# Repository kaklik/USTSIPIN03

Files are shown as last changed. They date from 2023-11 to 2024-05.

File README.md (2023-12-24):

## USTSIPIN03 - Semiconductor based ionizing radiation dosimeter and spectrometer analog front-end

The USTSIPIN03 is developed as single board improved variant of the [PIND02](https://github.com/mlab-modules/PIND02) and [PCRD07](https://github.com/mlab-modules/PCRD07) modules from [MLAB.cz development system](https://www.mlab.cz/).  The analog front end is core part of the [AIRDOS04 cosmic radiation detector and dosimeter](https://github.com/UniversalScientificTechnologies/AIRDOS04). 

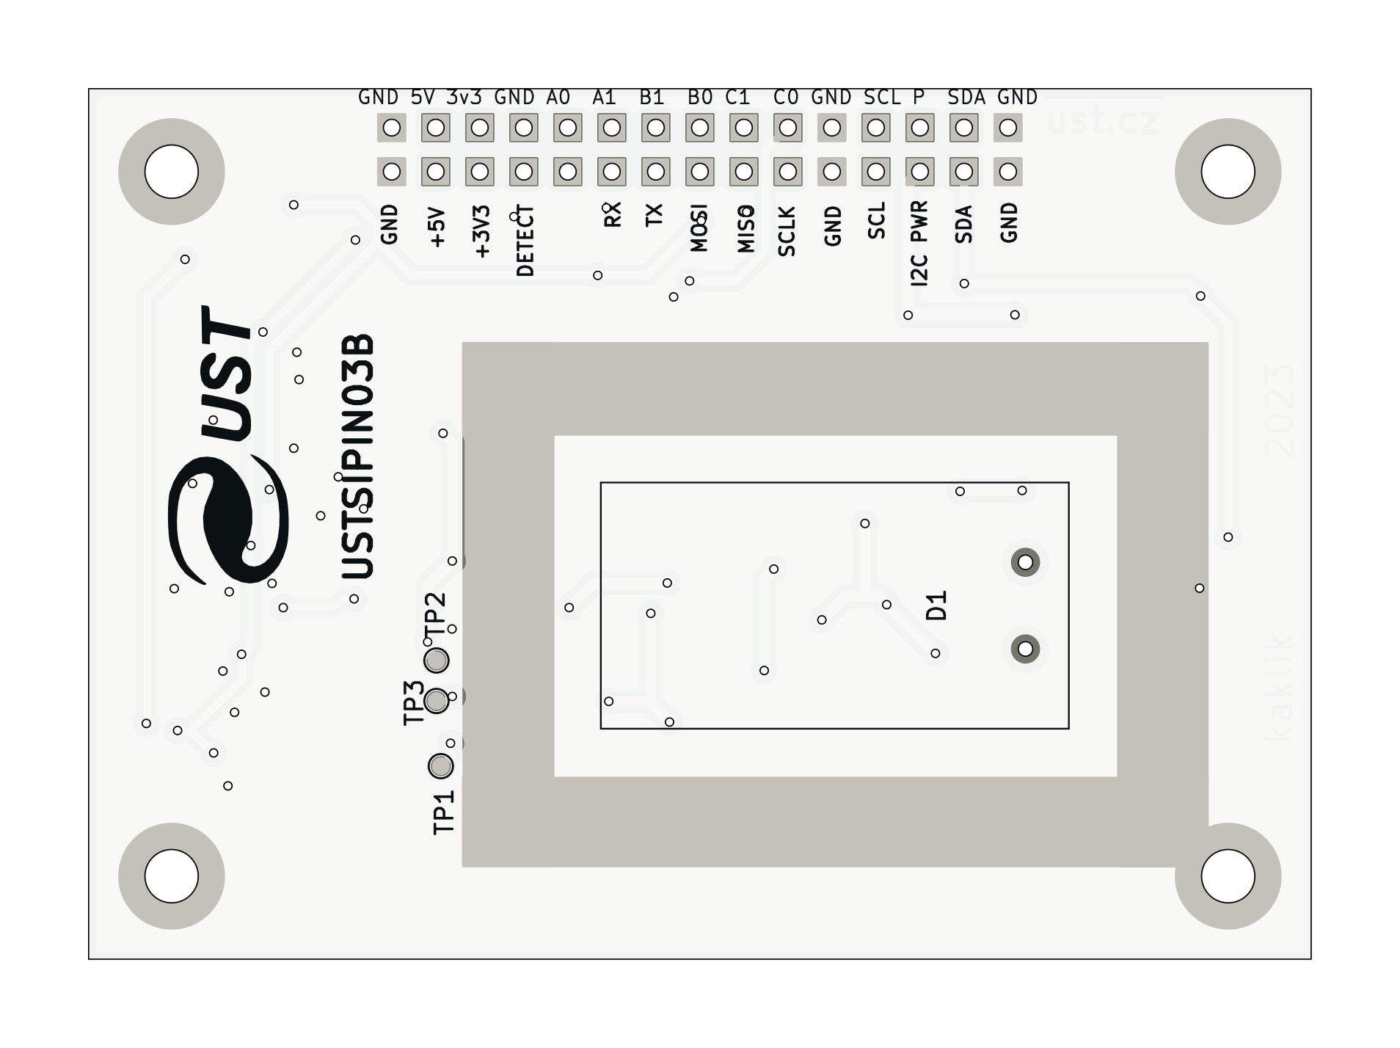
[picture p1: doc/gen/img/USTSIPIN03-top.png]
USTSIPIN03 Top view


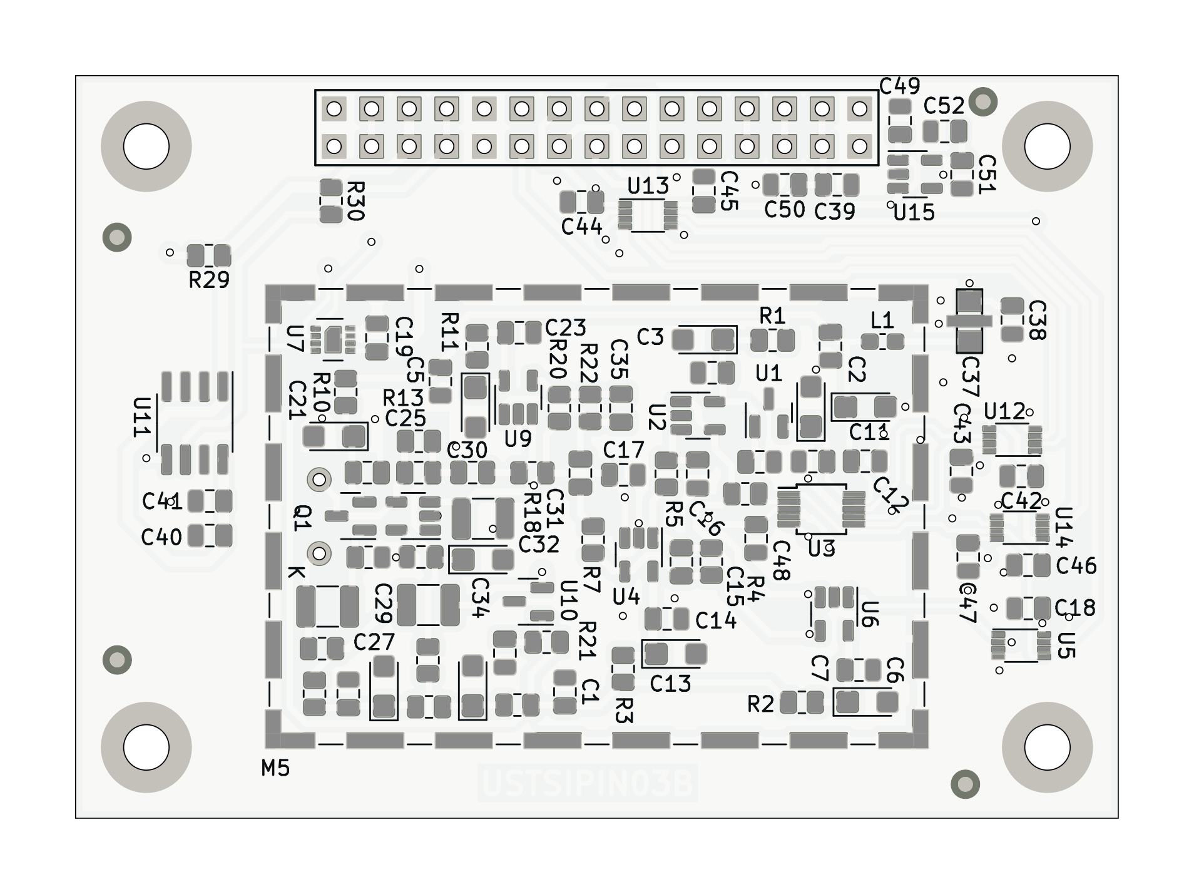
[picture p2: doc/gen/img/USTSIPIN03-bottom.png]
USTSIPIN03 Bottom view


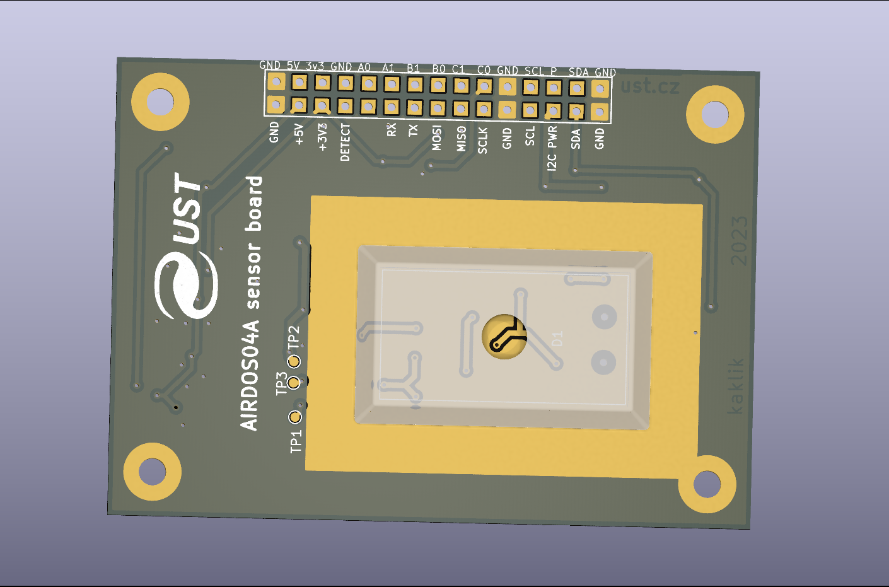
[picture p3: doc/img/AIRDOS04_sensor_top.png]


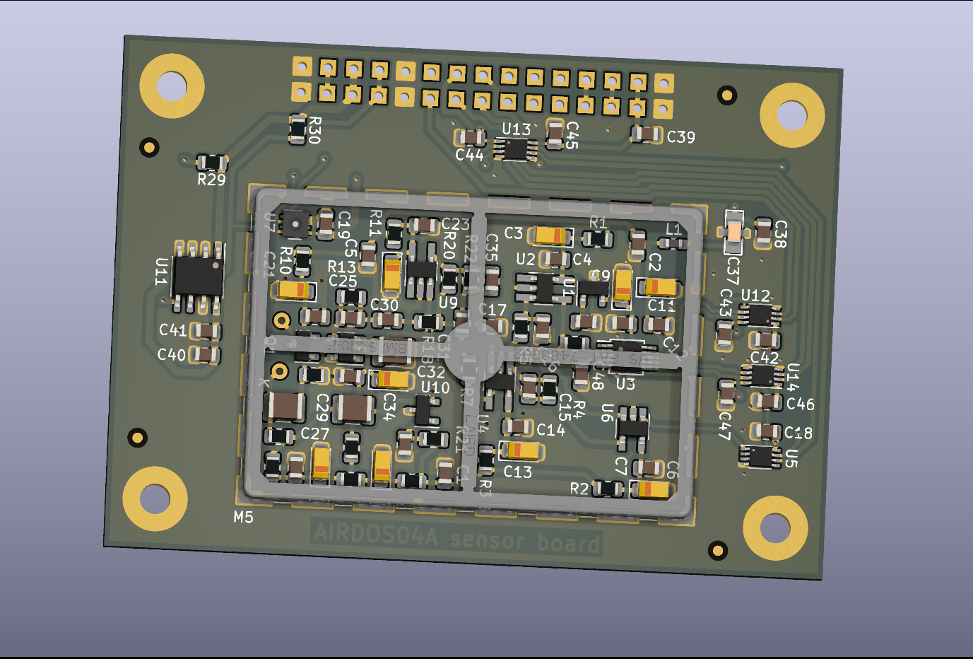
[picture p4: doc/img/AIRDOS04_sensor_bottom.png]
USTSIPIN03 Bottom view


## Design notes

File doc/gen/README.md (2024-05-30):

# PCB

Board size: 70.61x50.29 mm (2.78x1.98 inches)

- This is the size of the rectangle that contains the board
- Thickness: 1.6 mm (63 mils)
- Material: FR4
- Finish: HAL SnPb
- Layers: 2
- Copper thickness: 35 µm

Solder mask: TOP / BOTTOM

- Color: Green

Silk screen: TOP / BOTTOM

- Color: White

Stackup:

| Name                 | Type                 | Color            | Thickness | Material        | Epsilon_r | Loss tangent |
|----------------------|----------------------|------------------|-----------|-----------------|-----------|--------------|
| F.SilkS              | Top Silk Screen      |                  |           |                 |           |              |
| F.Mask               | Top Solder Mask      |                  |        10 |                 |           |              |
| F.Cu                 | copper               |                  |        35 |                 |           |              |
| dielectric 1         | core                 |                  |      1510 | FR4             |       4.5 |        0.020 |
| B.Cu                 | copper               |                  |        35 |                 |           |              |
| B.Mask               | Bottom Solder Mask   |                  |        10 |                 |           |              |
| B.Paste              | Bottom Solder Paste  |                  |           |                 |           |              |
| B.SilkS              | Bottom Silk Screen   |                  |           |                 |           |              |

# Important sizes

Clearance: 0.2 mm (8 mils)

Track width: 0.2 mm (8 mils)

- By design rules: 0.2 mm (8 mils)

Drill: 0.5 mm (20 mils)

- Vias: 0.5 mm (20 mils) [Design: 0.4 mm (16 mils)]
- Pads: 0.85 mm (33 mils)
- The above values are real drill sizes, they add 0.1 mm (4 mils) to plated holes (PTH)

Via: 0.8/0.4 mm (31/16 mils)

- By design rules: 0.8/0.3 mm (31/12 mils)
- Micro via: yes [0.2/0.1 mm (8/4 mils)]
- Buried/blind via: yes
- Total: 59 (thru: 59 buried/blind: 0 micro: 0)

Outer Annular Ring: 0.15 mm (6 mils)

- By design rules: 0.26 mm (10 mils)

Eurocircuits class: 4B
- Using min drill 0.5 mm for an OAR of 0.15 mm

# General stats

Components count: (SMD/THT)

- Top: 0/6 (THT)
- Bottom: 96/1 (SMD + THT)

Defined tracks:

- 0.2 mm (8 mils)
- 0.3 mm (12 mils)
- 0.4 mm (16 mils)
- 0.5 mm (20 mils)
- 0.6 mm (24 mils)
- 0.7 mm (28 mils)
- 0.8 mm (31 mils)

Used tracks:

- 0.2 mm (8 mils) (2) defined: yes
- 0.3 mm (12 mils) (136) defined: yes
- 0.4 mm (16 mils) (75) defined: yes
- 0.45 mm (18 mils) (443) defined: no
- 0.5 mm (20 mils) (4) defined: yes
- 0.6 mm (24 mils) (24) defined: yes
- 0.7 mm (28 mils) (30) defined: yes

Defined vias:

Used vias:

- 0.8/0.4 mm (31/16 mils) (Count: 59, Aspect: 2.0 A) defined: no

Holes (excluding vias):

- 0.76 mm (30 mils) (2)
- 0.89 mm (35 mils) (30)
- 3.0 mm (118 mils) (4)

Oval holes:

Drill tools (including vias and computing adjusts and rounding):

- 0.5 mm (20 mils) (59)
- 0.85 mm (33 mils) (2)
- 1.0 mm (39 mils) (30)
- 3.1 mm (122 mils) (4)

Solder paste stats:

Using a paste with 87.75 % alloy, that has an specific gravity for the alloy of 7.4 g/cm³
and 1.0 g/cm³ for the flux. This paste has an specific gravity of  4.15 g/cm³.

The stencil thickness is  0.12 mm.

| Side   | Pads with paste | Area [mm²] | Paste [g] |
|--------|-----------------|------------|-----------|
| Total  |             281 |     379.06 |      1.89 |

Note: this is just an approximation to the theoretical value. Margins of the solder mask and waste aren't computed.

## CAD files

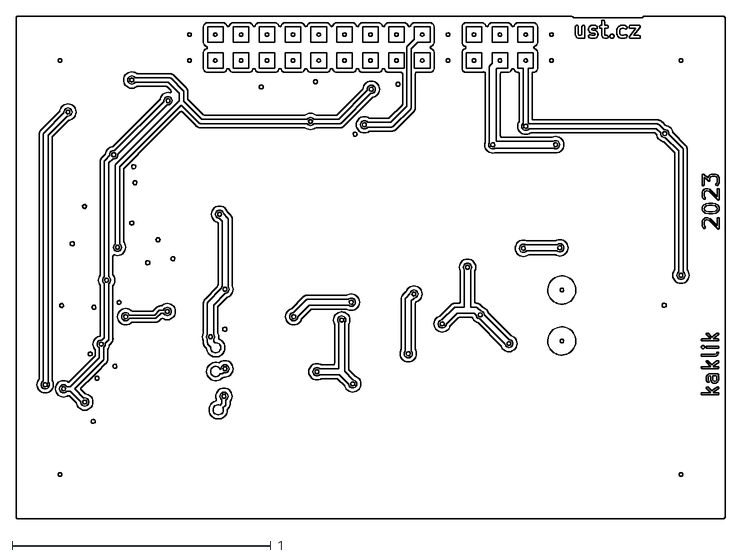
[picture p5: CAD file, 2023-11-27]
doc/gen/dxf/USTSIPIN03-F_Cu.dxf
2.74 x 1.94

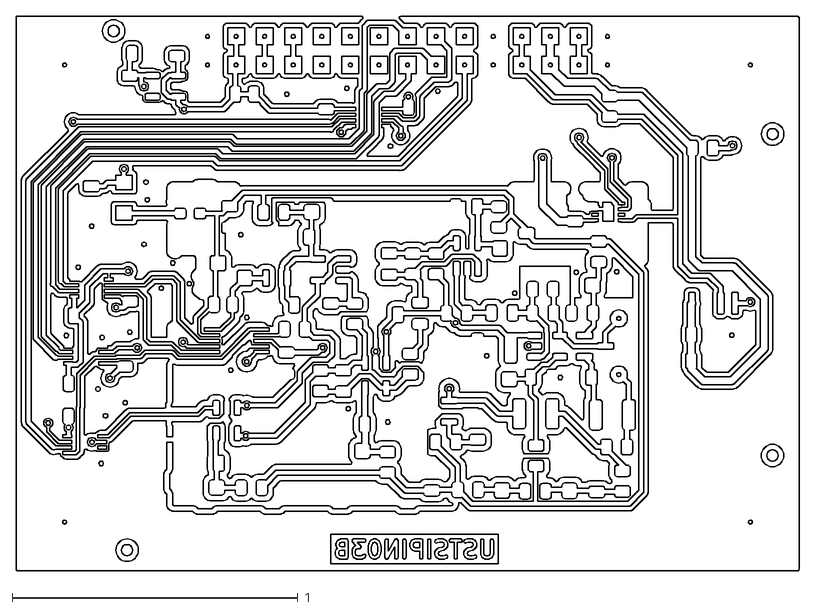
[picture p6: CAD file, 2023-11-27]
doc/gen/dxf/USTSIPIN03-B_Cu.dxf
2.74 x 1.94

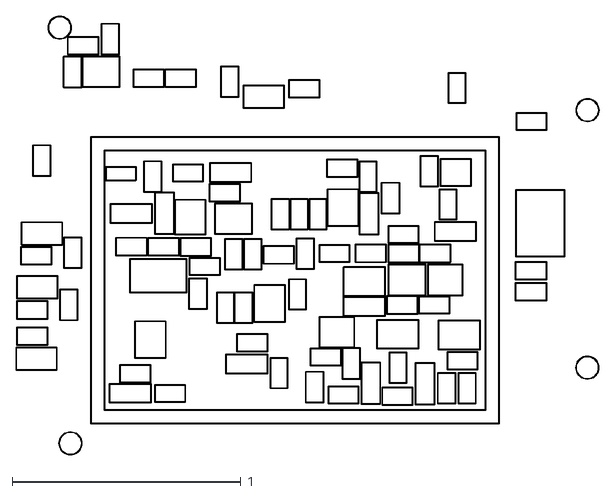
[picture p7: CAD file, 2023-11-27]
doc/gen/dxf/USTSIPIN03-B_Courtyard.dxf
2.55 x 1.92

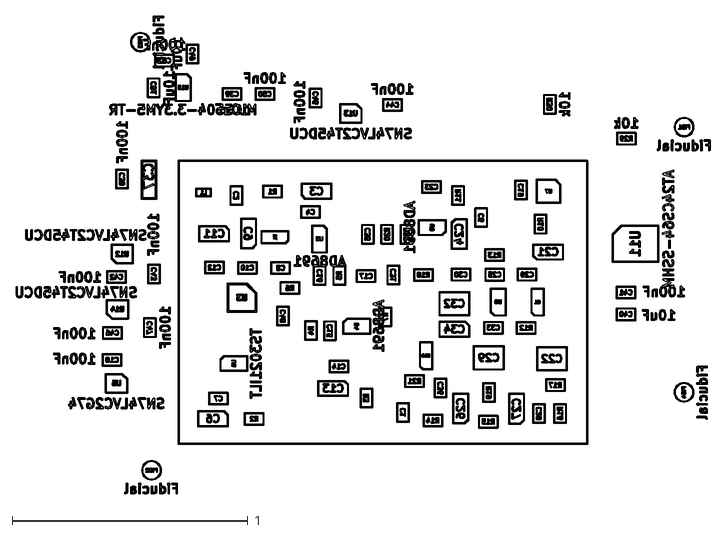
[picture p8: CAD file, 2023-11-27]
doc/gen/dxf/USTSIPIN03-B_Fab.dxf
2.94 x 2.03

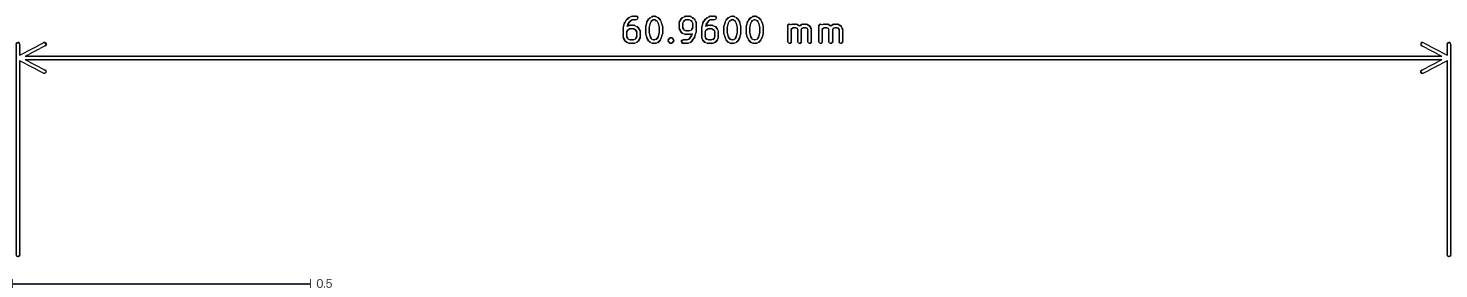
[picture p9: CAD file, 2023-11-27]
doc/gen/dxf/USTSIPIN03-User_Comments.dxf
2.41 x 0.403

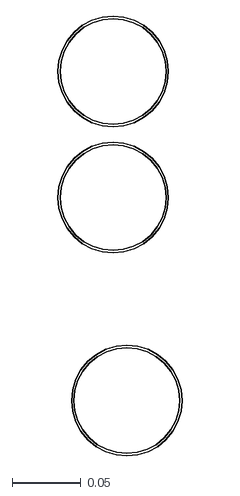
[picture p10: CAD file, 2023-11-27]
doc/gen/dxf/USTSIPIN03-F_Courtyard.dxf
0.0907 x 0.321

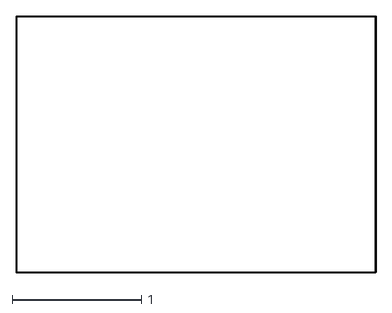
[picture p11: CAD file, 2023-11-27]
doc/gen/dxf/USTSIPIN03-Edge_Cuts.dxf
2.79 x 1.99

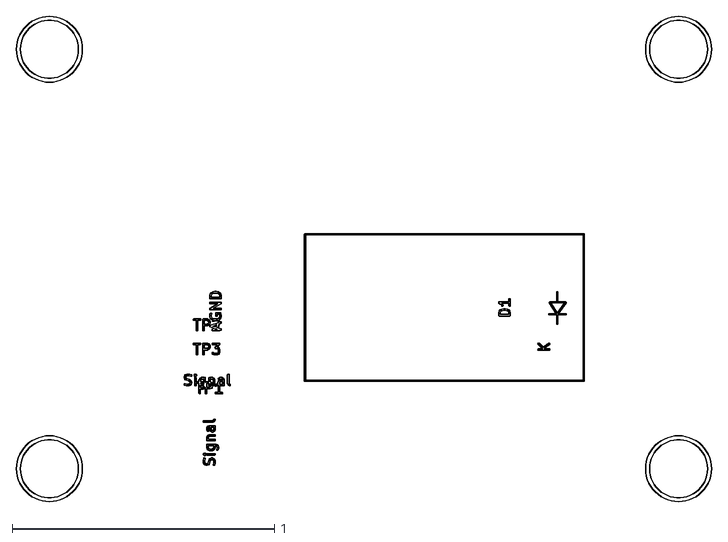
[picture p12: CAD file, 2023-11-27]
doc/gen/dxf/USTSIPIN03-F_Fab.dxf
2.65 x 1.85

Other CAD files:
doc/gen/dxf/USTSIPIN03-User_Drawings.dxf
doc/gen/dxf/USTSIPIN03-Margin.dxf
doc/gen/dxf/USTSIPIN03-B_Mask.dxf
doc/gen/dxf/USTSIPIN03-B_Paste.dxf
doc/gen/dxf/USTSIPIN03-B_Silkscreen.dxf
doc/gen/dxf/USTSIPIN03-F_Mask.dxf
doc/gen/dxf/USTSIPIN03-F_Silkscreen.dxf

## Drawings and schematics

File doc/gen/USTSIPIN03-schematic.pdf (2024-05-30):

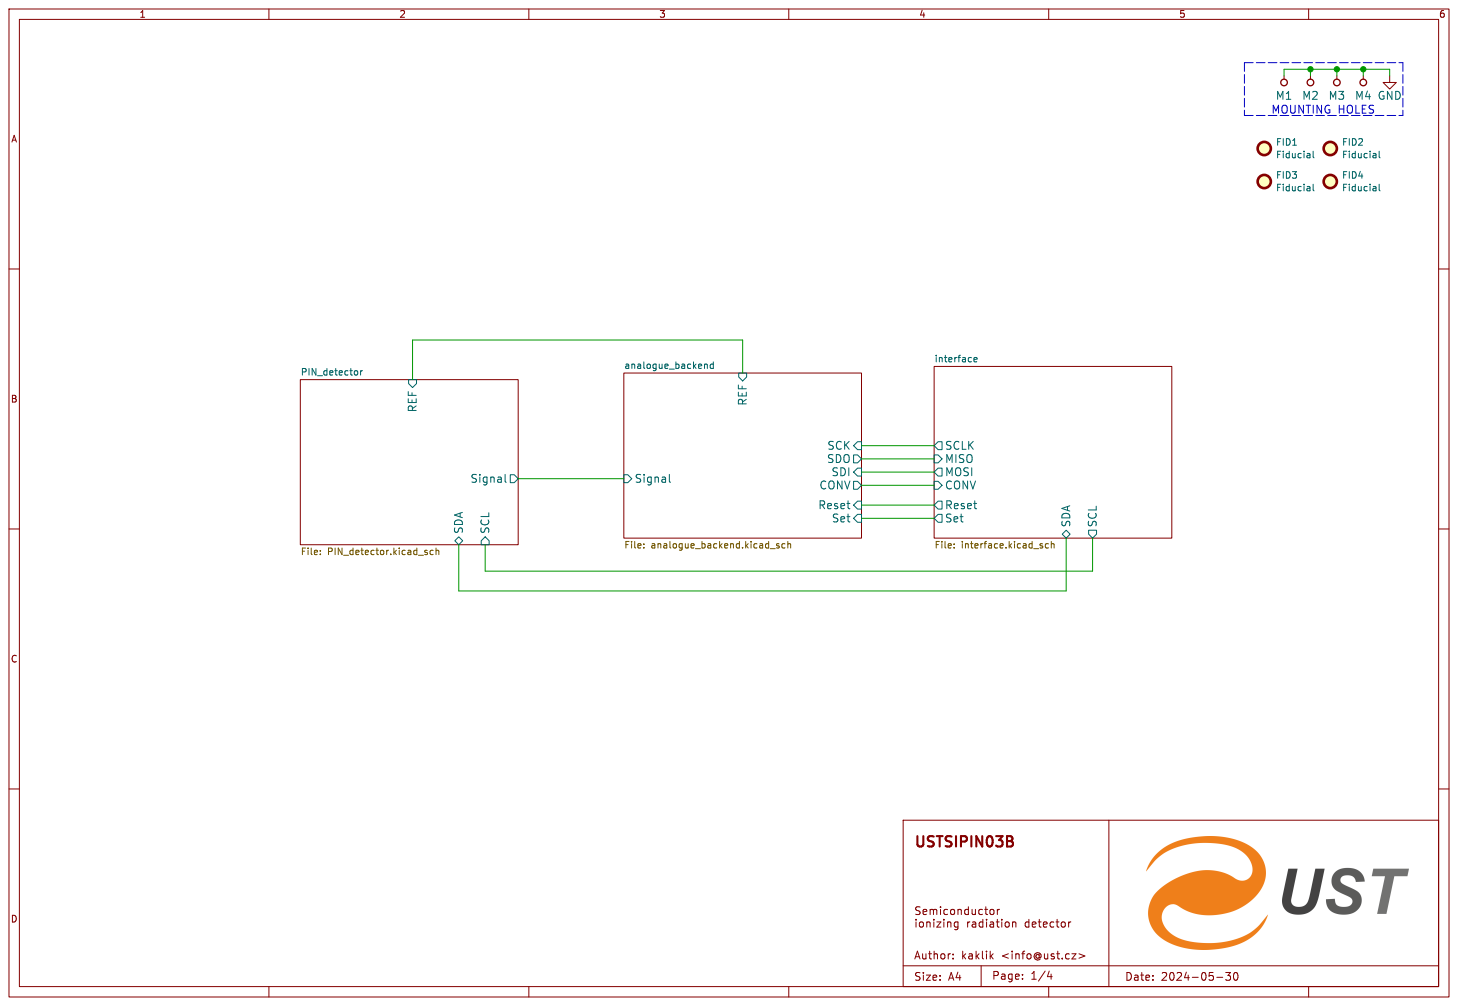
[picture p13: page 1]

FID2 Fiducial FID3 Fiducial FID1 Fiducial M1 MOUNTING HOLES

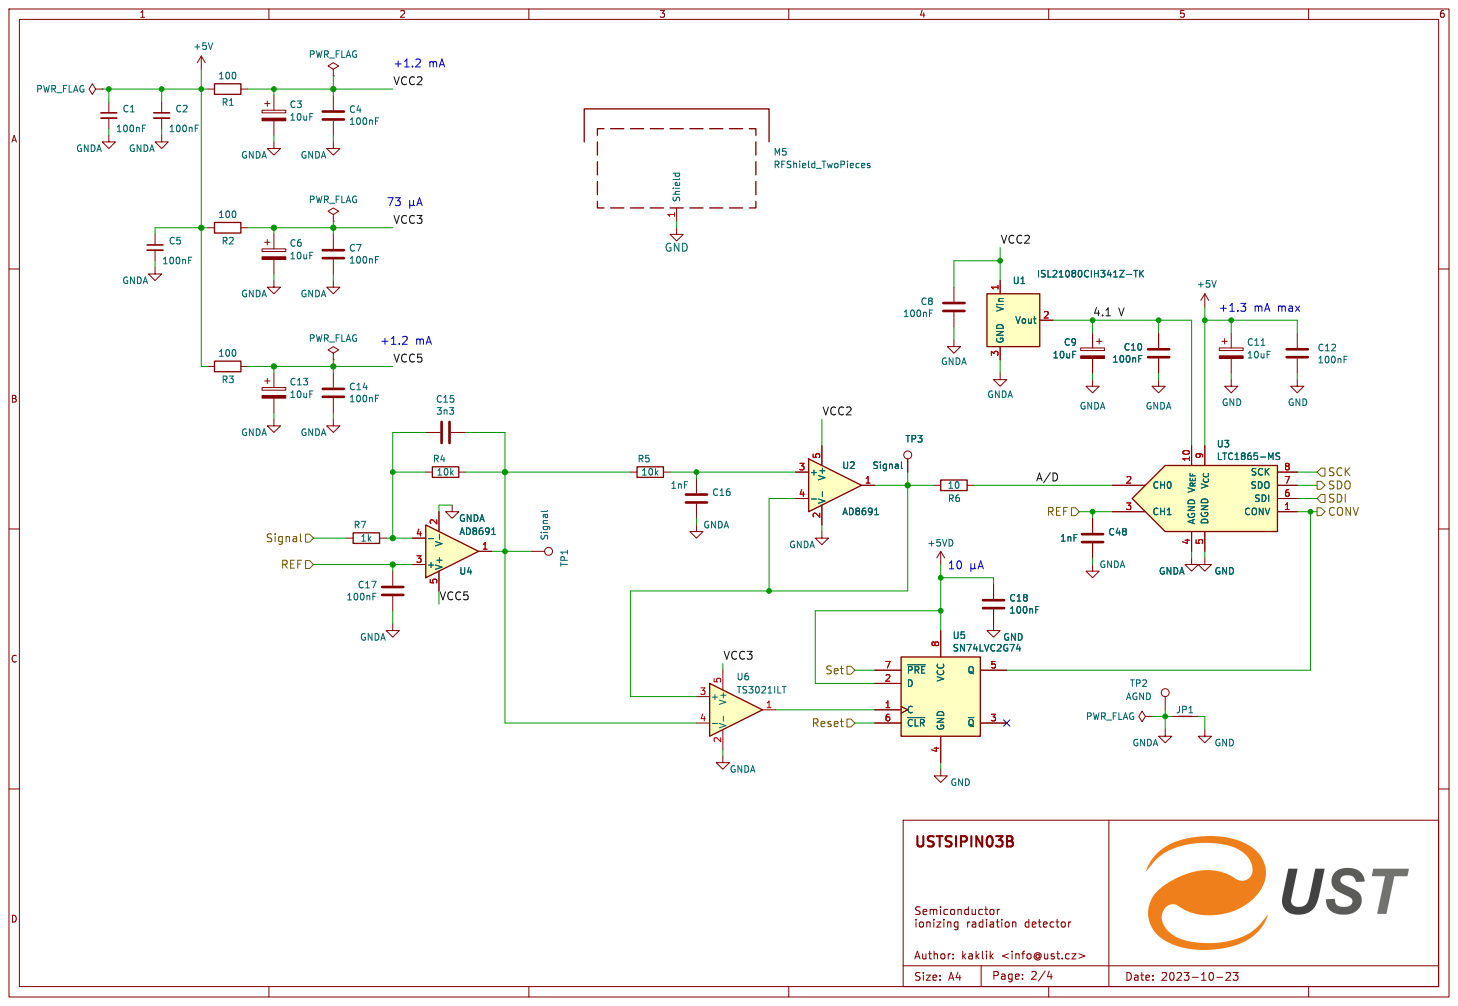
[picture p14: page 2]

5 SDI 6 SDO 7 SCK 8 V_{CC}9 U3
LTC1865-MS

5 SDI 6 SDO 7 SCK 8 V_{CC}9 GNDA GND

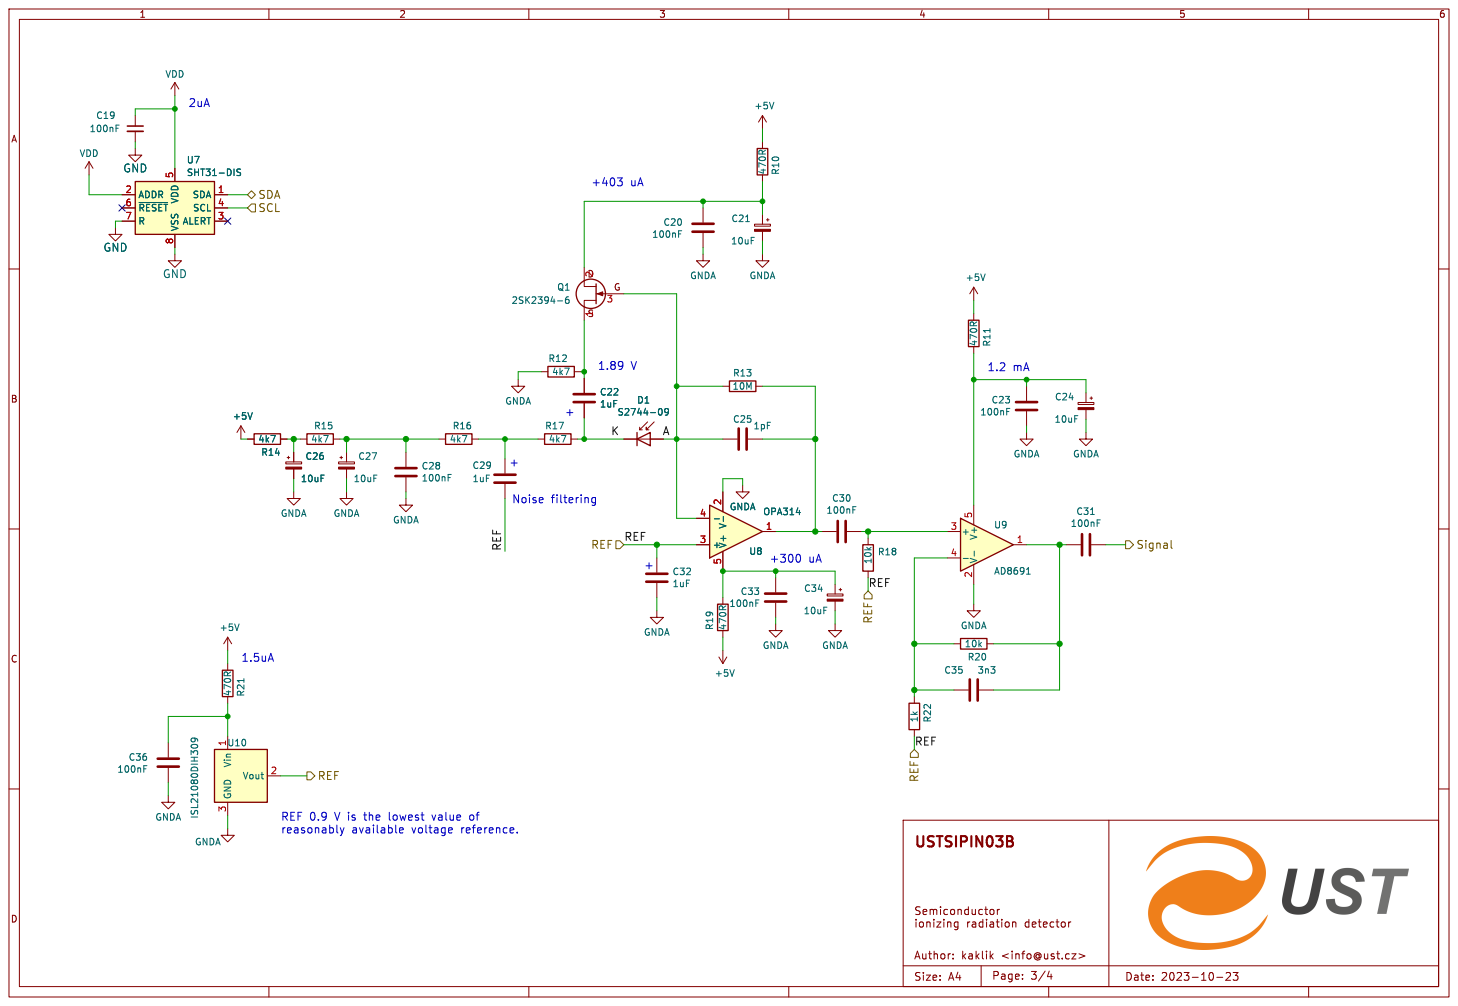
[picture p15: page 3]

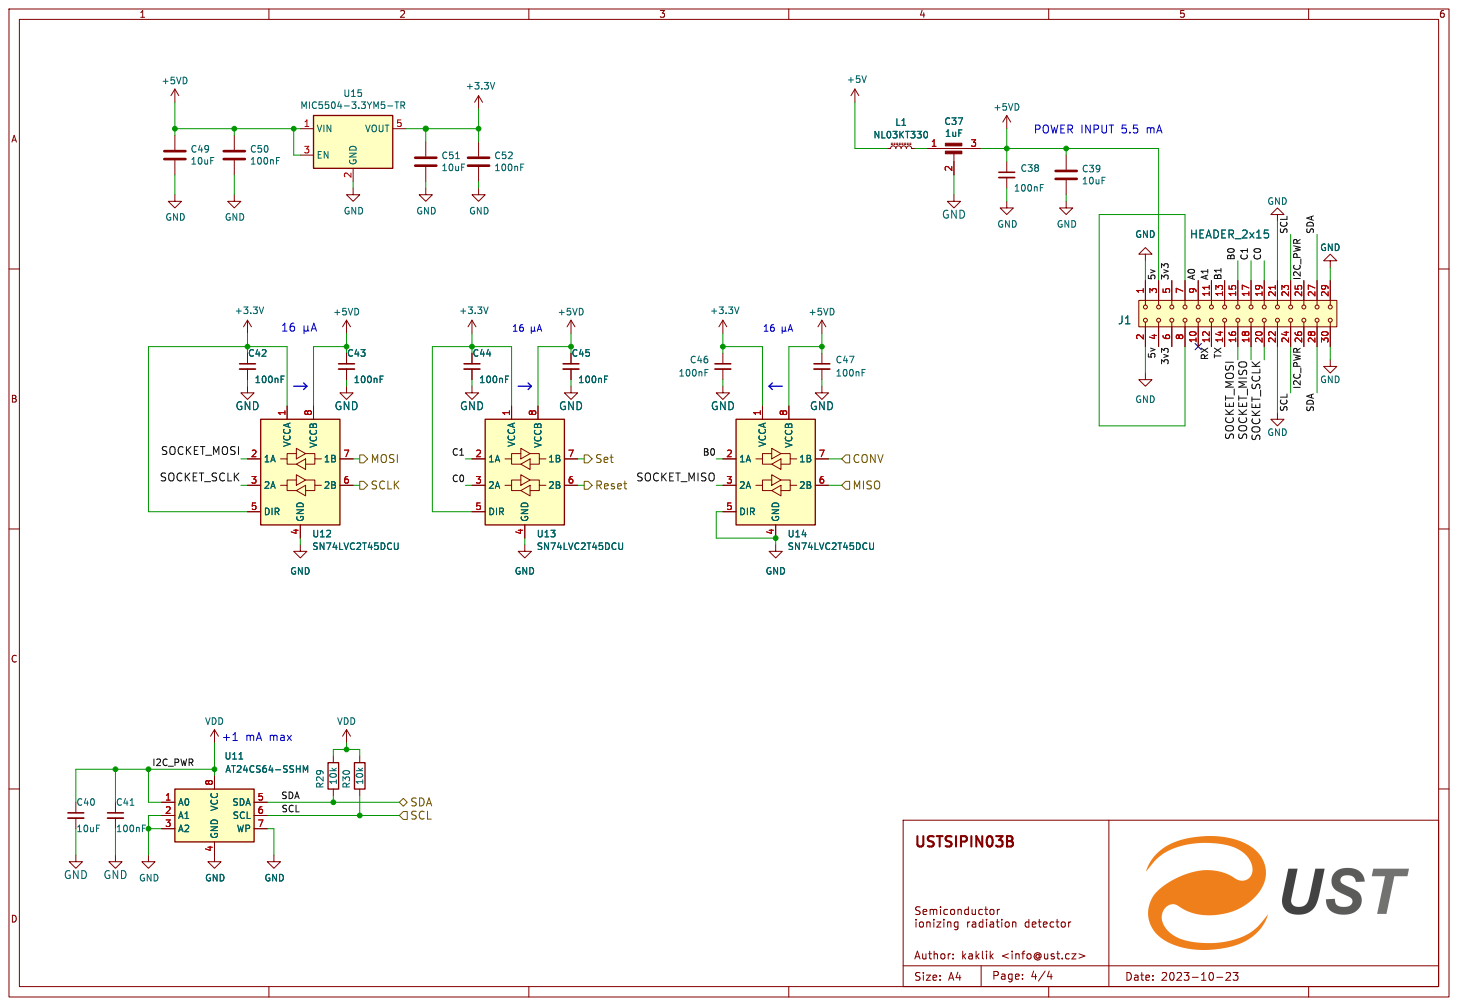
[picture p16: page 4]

VDD GND GND GND

4 SDA 5 SCL 6 WP 7 VCC

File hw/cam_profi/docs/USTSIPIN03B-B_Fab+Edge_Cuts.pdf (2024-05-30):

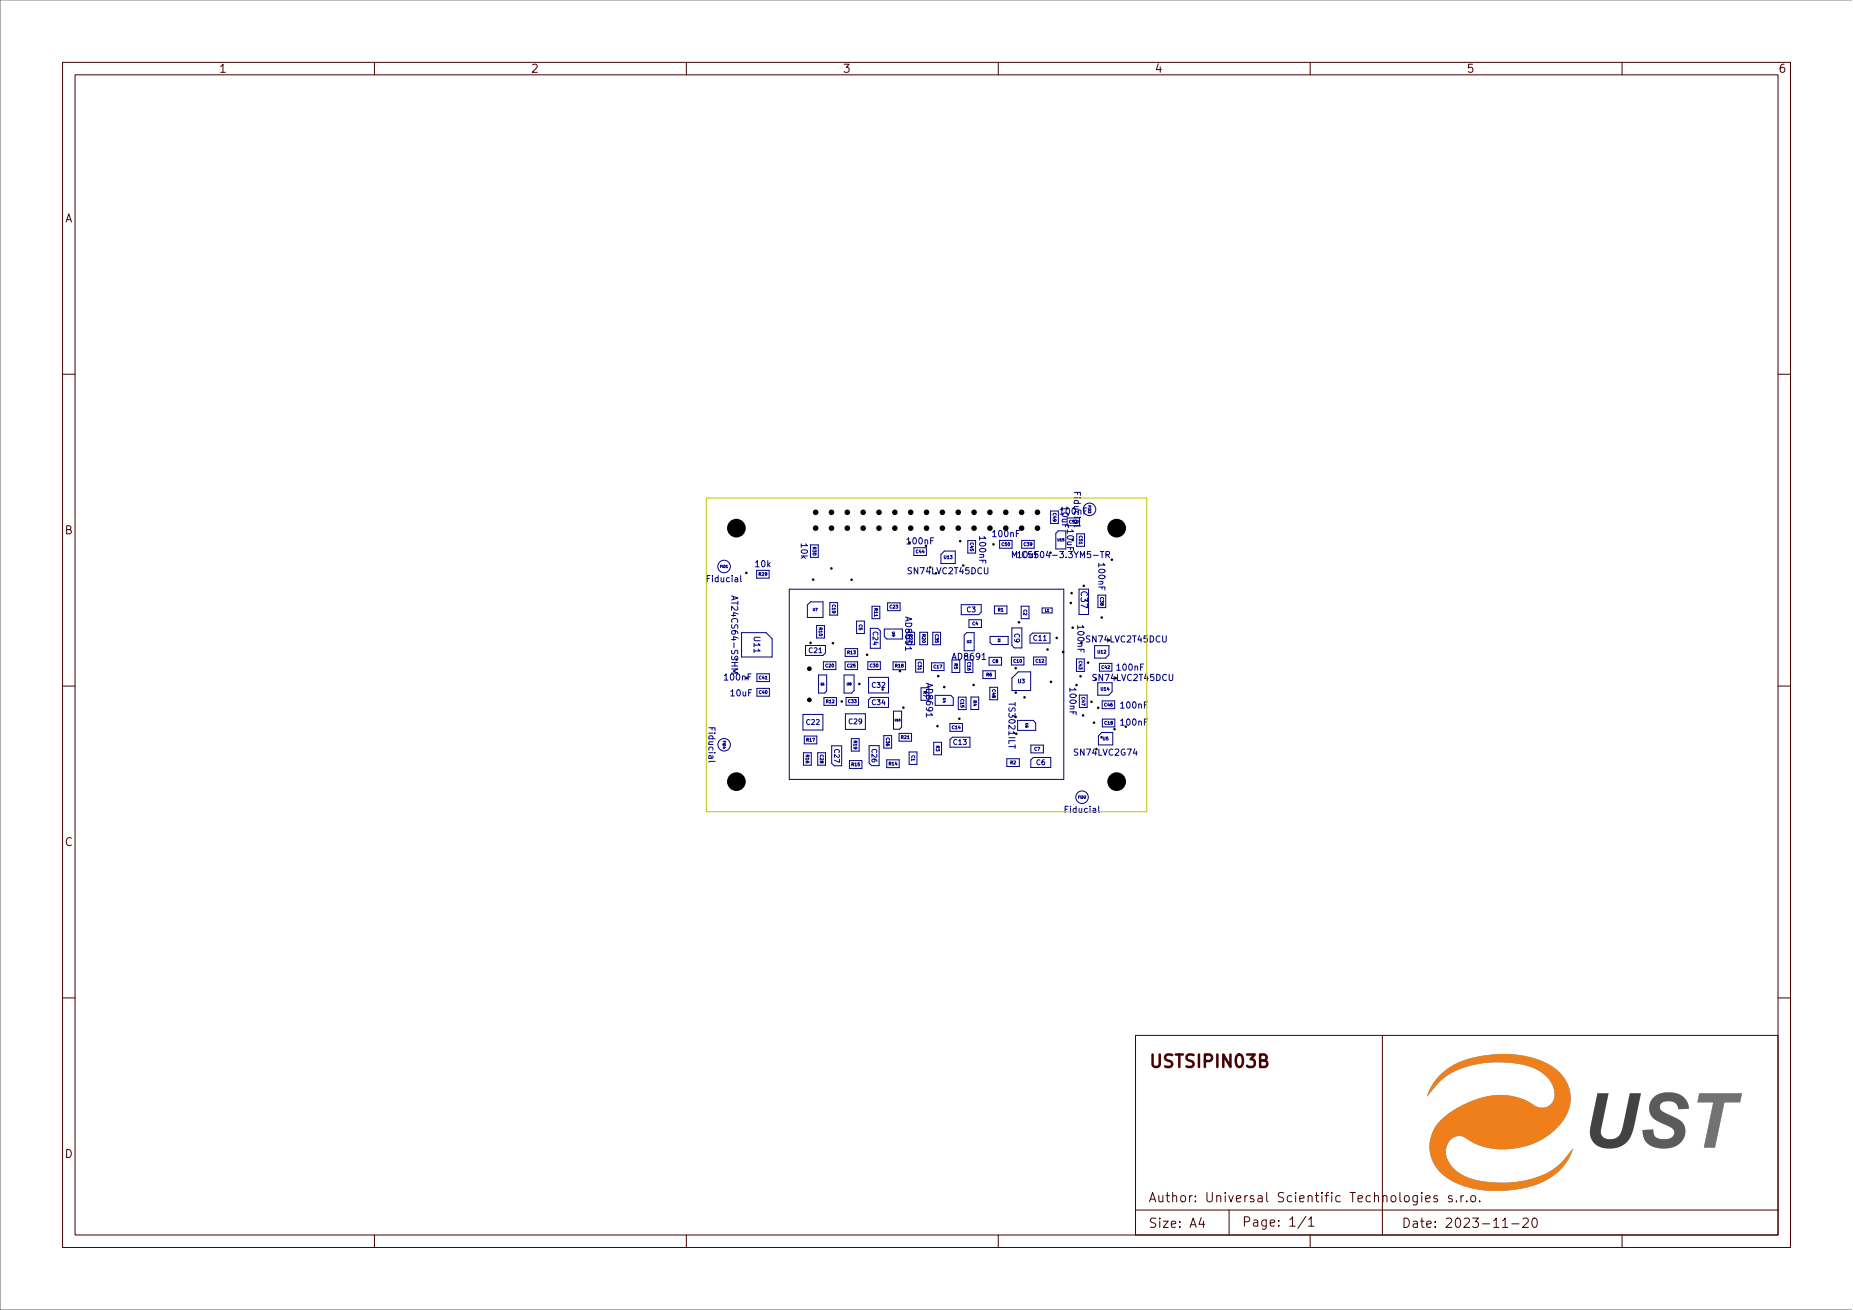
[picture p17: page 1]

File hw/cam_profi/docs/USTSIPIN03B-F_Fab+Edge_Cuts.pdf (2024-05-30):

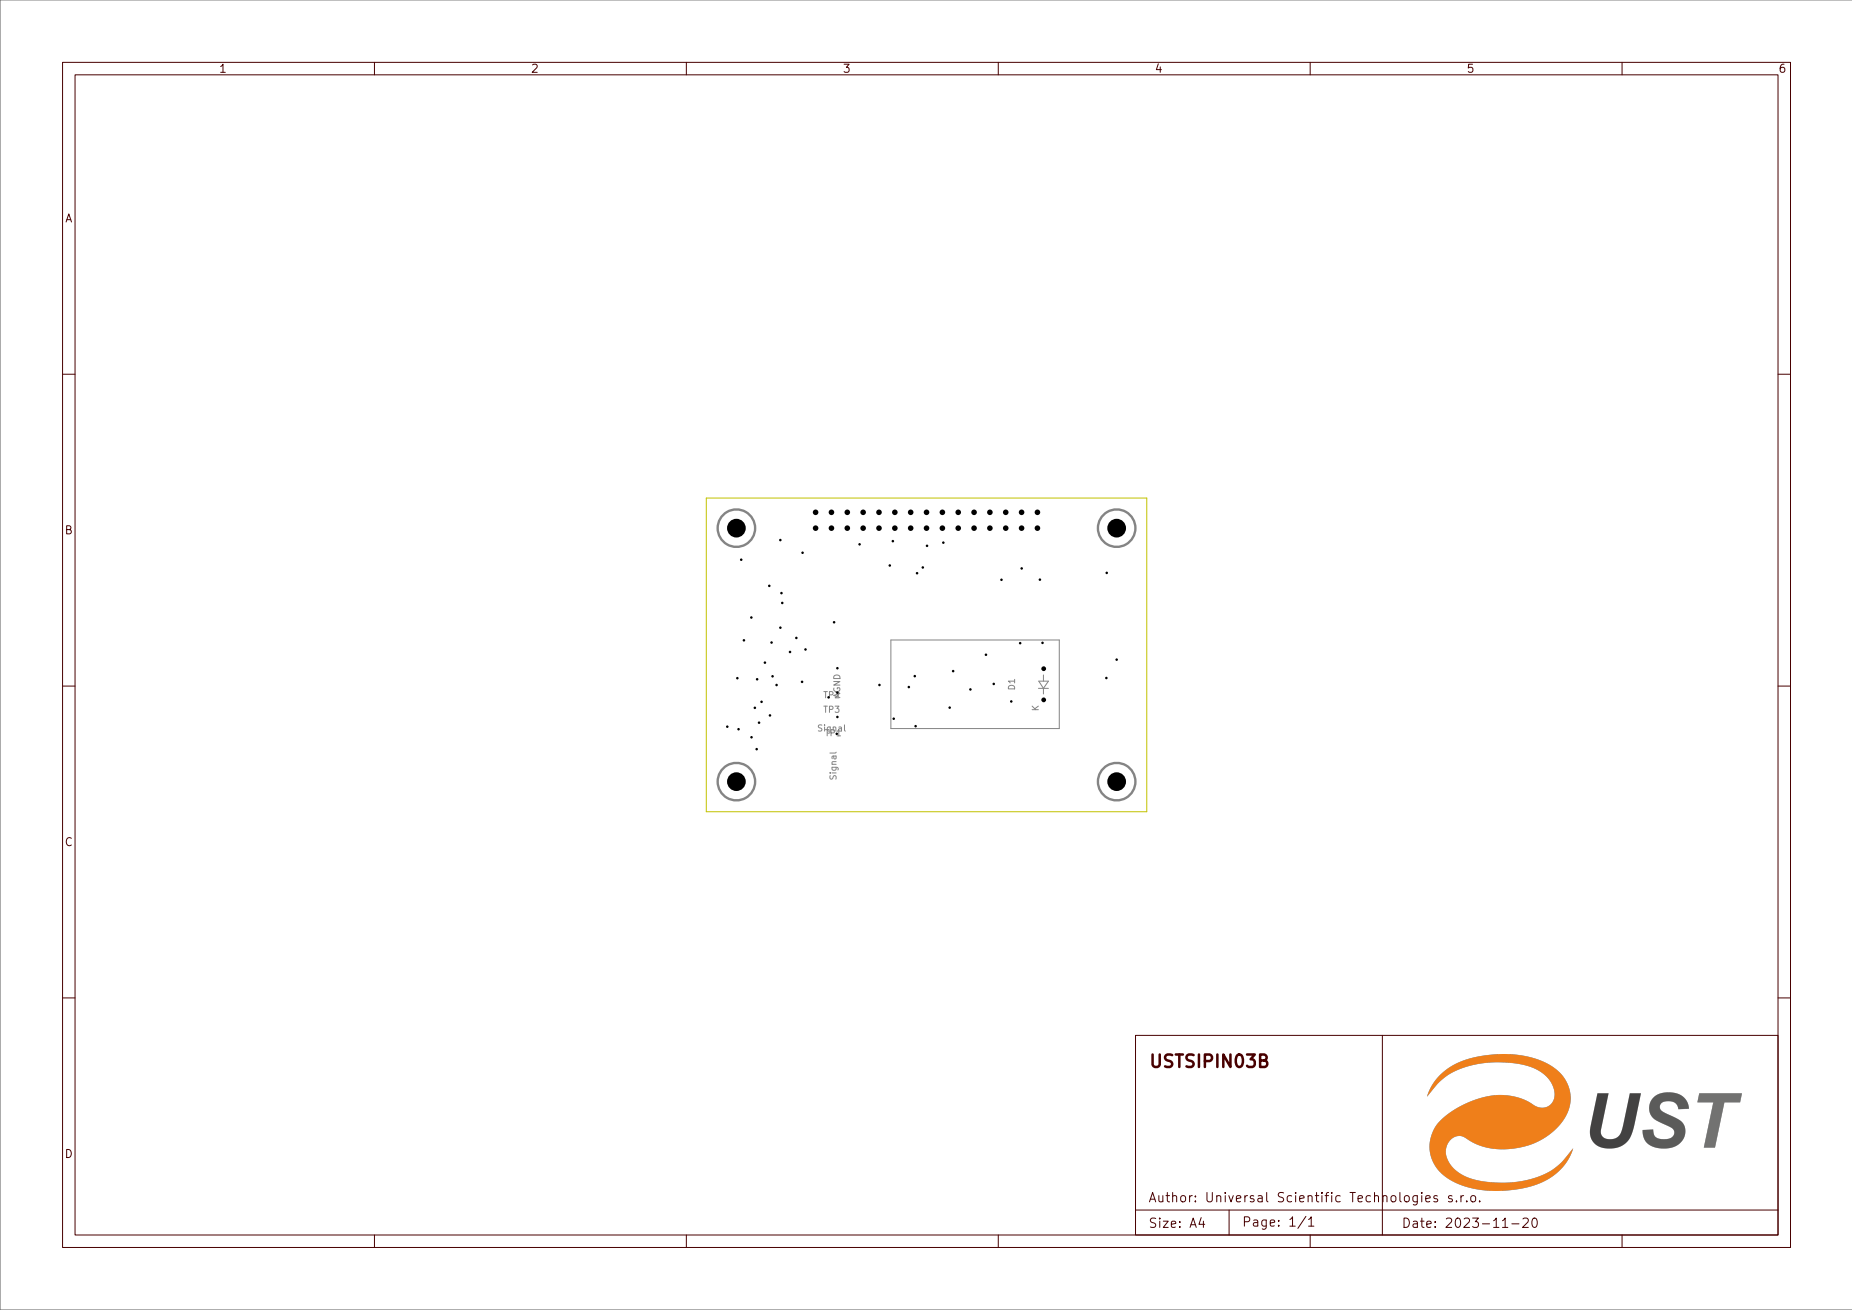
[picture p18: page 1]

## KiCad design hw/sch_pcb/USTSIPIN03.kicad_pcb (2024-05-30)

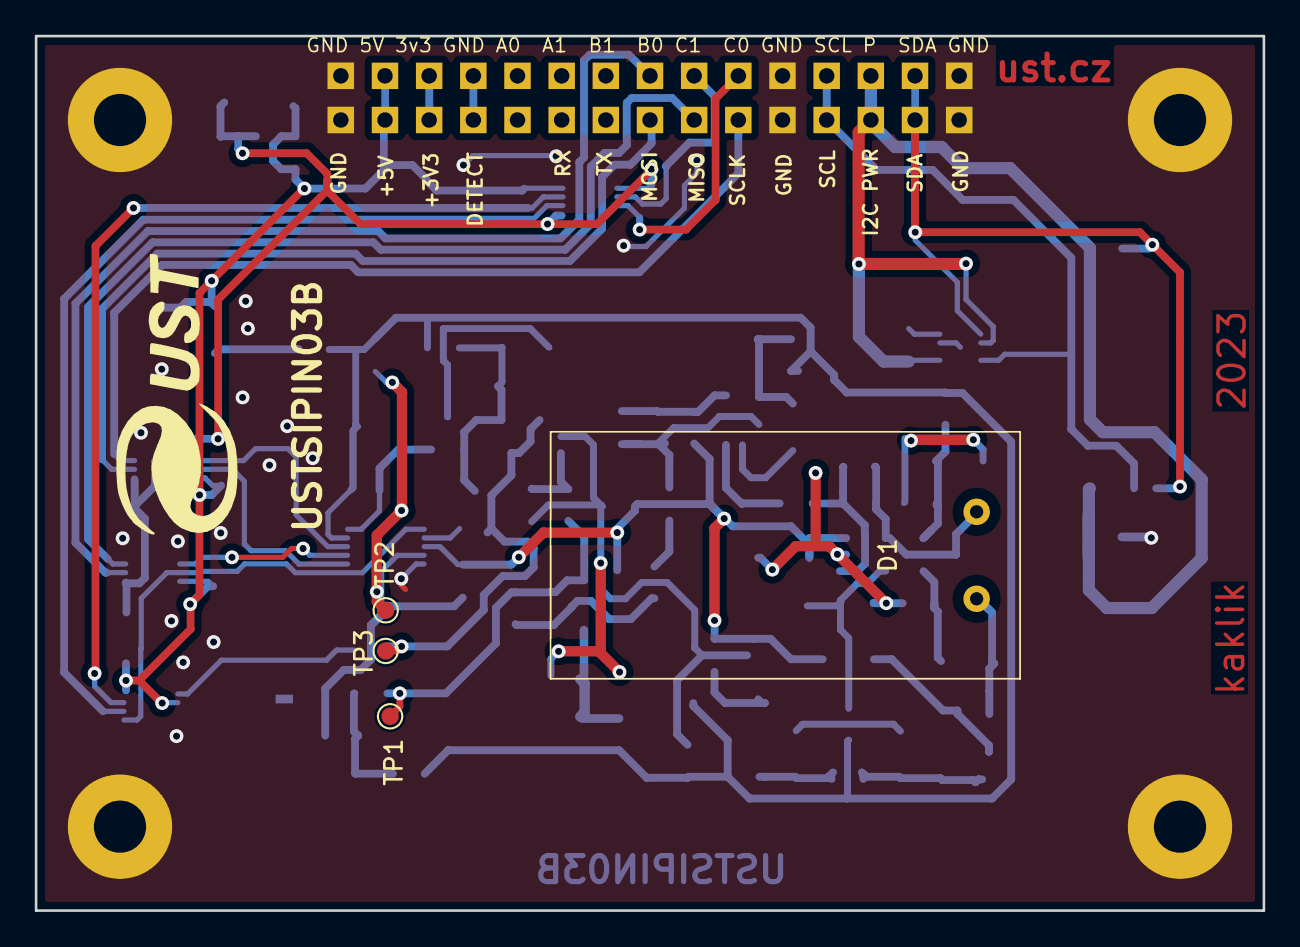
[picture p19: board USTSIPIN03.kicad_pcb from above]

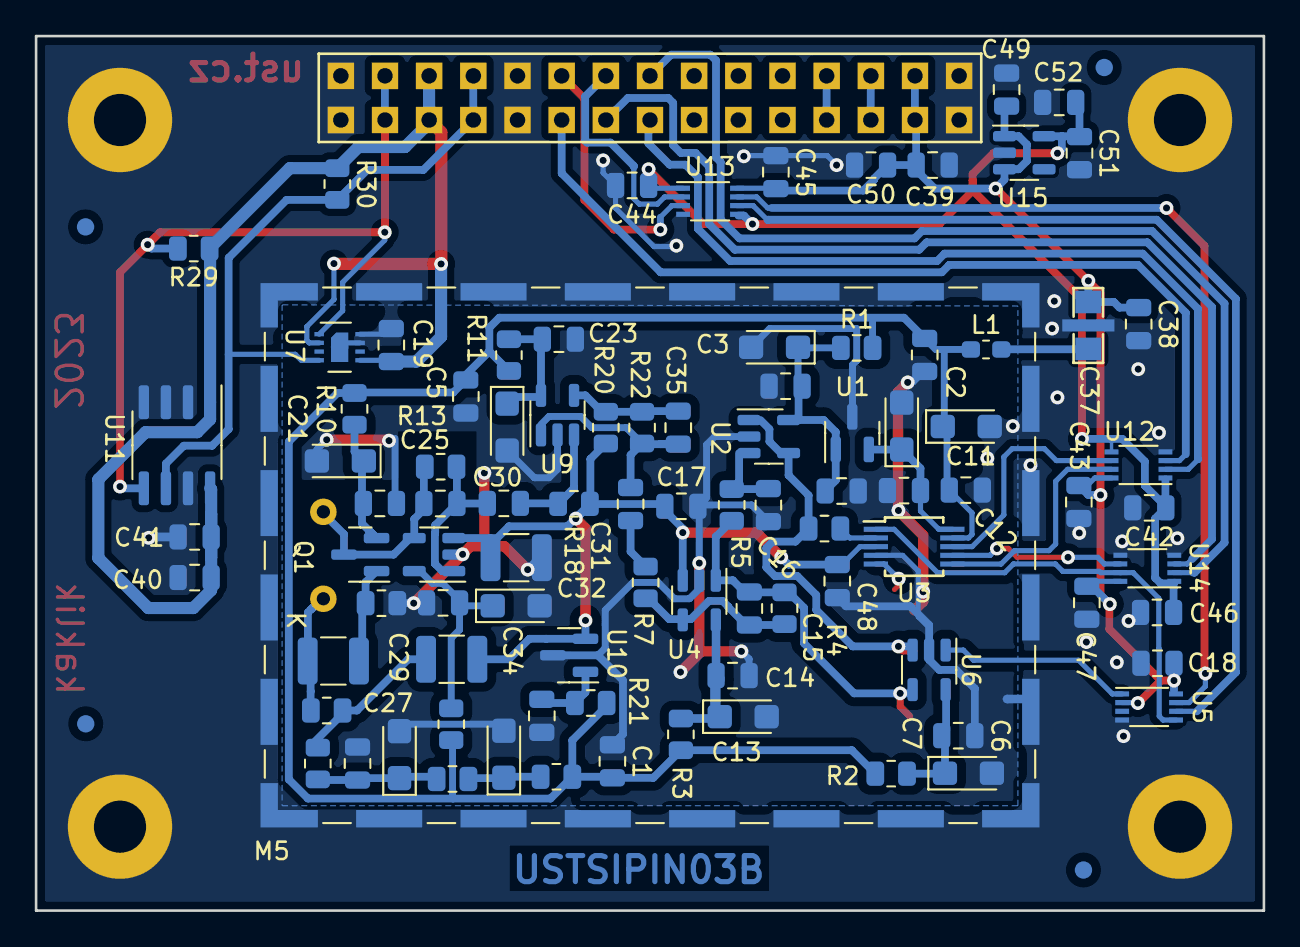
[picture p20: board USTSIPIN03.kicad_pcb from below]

Board: 2 copper layers, 70.6 x 50.3 mm, 107 parts (98 on the bottom side), 49 nets.

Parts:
C1, C2, C4, C5, C7, C8, C10, C12, C14, C17, C18, C19, C20, C23, C28, C30, C31, C33, C36, C38, C41, C42, C43, C44, C45, C46, C47, C50, C52: 100nF; C_0805_2012Metric
C3, C6, C9, C11, C13, C21, C24, C26, C27, C34: 10uF; CP_EIA-3216-18_Kemet-A
C15, C35: 3n3; C_0805_2012Metric
C16, C48: 1nF; C_0805_2012Metric
C22, C29, C32: 1uF; C_1210_3225Metric
C25: 1pF; C_0805_2012Metric
C37: 1uF; FIR_0805
C39, C40, C49, C51: 10uF; C_0805_2012Metric
D1: S2744-09; HAMAMATSU_S2744-09
FID1, FID2, FID3, FID4: Fiducial; Fiducial_1mm_Mask2mm
G1: LOGO; UST
J1: HEADER_2x15; Straight_2x15
JP1: Jumper_2_Bridged; NetTie-2_SMD_Pad0.5mm
L1: NL03KT330; L_0603_1608Metric_Pad1.05x0.95mm_HandSolder
M1, M2, M3, M4: HOLE; MountingHole_3mm
M5: RFShield_TwoPieces; Laird_Technologies_BMI-S-210-F_44.00x30.50mm
Q1: 2SK2394-6; SOT-23
R1, R2, R3: 100; R_0805_2012Metric
R4, R5, R18, R20, R29, R30: 10k; R_0805_2012Metric
R6: 10; R_0805_2012Metric
R7, R22: 1k; R_0805_2012Metric
R10, R11, R19, R21: 470R; R_0805_2012Metric
R12, R14, R15, R16, R17: 4k7; R_0805_2012Metric
R13: 10M; R_0805_2012Metric
TP1, TP3: Signal; TestPoint_Pad_D1.0mm
TP2: AGND; TestPoint_Pad_D1.0mm
U1: ISL21080CIH341Z-TK; SOT-23
U2, U4, U9: AD8691; TSOT-23-5
U3: LTC1865-MS; MSOP-10_3x3mm_P0.5mm
U5: SN74LVC2G74; VSSOP-8_2.3x2mm_P0.5mm
U6: TS3021ILT; SOT-23-5
U7: SHT31-DIS; Sensirion_DFN-8-1EP_2.5x2.5mm_P0.5mm_EP1.1x1.7mm
U8: OPA314; SOT-23-5
U10: ISL21080DIH309; SOT-23
U11: AT24CS64-SSHM; SOIC-8_3.9x4.9mm_P1.27mm
U12, U13, U14: SN74LVC2T45DCU; VSSOP-8_2.3x2mm_P0.5mm
U15: MIC5504-3.3YM5-TR; SOT-23-5

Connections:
+3.3V: C42.1, C44.1, C46.1, C51.1, C52.1, U12.1 (VCCA), U12.5 (DIR), U13.1 (VCCA), U13.5 (DIR), U14.1 (VCCA), U15.5 (VOUT)
+5V: C1.1, C2.1, C5.1, C11.1, C12.1, L1.1, R1.2, R2.2, R3.2, R10.2, R11.2, R14.2, R19.2, R21.2, U3.9 (V_{CC})
+5VD: C18.1, C37.3, C38.1, C39.1, C43.1, C45.1, C47.1, C49.1, C50.1, J1.3, J1.4, U5.2 (D), U5.8 (VCC), U12.8 (VCCB), U13.8 (VCCB), U14.8 (VCCB), U15.1 (VIN), U15.3 (EN)
/PIN_detector/A: C25.2, D1.2 (A), Q1.3 (G), R13.2, U8.4 (-)
/PIN_detector/K: C22.2, D1.1 (K), R17.1
/PIN_detector/REF: C17.1, C29.2, C32.1, C48.1, R18.1, R22.2, U3.3 (CH1), U4.3 (+), U8.3 (+), U10.2 (Vout)
/PIN_detector/Signal: C31.1, R7.2
/analogue_backend/4.1 V: C9.1, C10.1, U1.2 (Vout), U3.10 (V_{REF})
/analogue_backend/A/D: R6.1, U3.2 (CH0)
/analogue_backend/CONV: U3.1 (CONV), U5.5 (Q), U14.7 (1B)
/analogue_backend/Reset: U5.6 (~CLR), U13.6 (2B)
/analogue_backend/SCK: U3.8 (SCK), U12.6 (2B)
/analogue_backend/SDI: U3.6 (SDI), U12.7 (1B)
/analogue_backend/SDO: U3.7 (SDO), U14.6 (2B)
/analogue_backend/Set: U5.7 (~PRE), U13.7 (1B)
/analogue_backend/VCC2: C3.1, C4.1, C8.1, R1.1, U1.1 (Vin), U2.5 (V+)
/analogue_backend/VCC3: C6.1, C7.1, R2.1, U6.5 (V+)
/analogue_backend/VCC5: C13.1, C14.1, R3.1, U4.5 (V+)
/interface/3v3: J1.5, J1.6
/interface/B0: J1.15, U14.2 (1A)
/interface/C0: J1.19, U13.3 (2A)
/interface/C1: J1.17, U13.2 (1A)
/interface/SCL: J1.23, J1.24, R30.2, U7.4 (SCL), U11.6 (SCL)
/interface/SDA: J1.27, J1.28, R29.2, U7.1 (SDA), U11.5 (SDA)
/interface/SOCKET_MISO: J1.18, U14.3 (2A)
/interface/SOCKET_MOSI: J1.16, U12.2 (1A)
/interface/SOCKET_SCLK: J1.20, U12.3 (2A)
GND: C11.2, C12.2, C18.2, C19.2, C37.2, C38.2, C39.2, C40.2, C41.2, C42.2, C43.2, C44.2, C45.2, C46.2, C47.2, C49.2, C50.2, C51.2, C52.2, J1.1, J1.2, J1.21, J1.22, J1.29, J1.30, JP1.2, M1.1, M2.1, M3.1, M4.1, M5.1 (Shield), U3.5 (DGND), U5.4 (GND), U7.7 (R), U7.8 (VSS), U7.9 (VSS), U11.2 (A1), U11.3 (A2), U11.4 (GND), U11.7 (WP), U12.4 (GND), U13.4 (GND), U14.4 (GND), U14.5 (DIR), U15.2 (GND)
GNDA: C1.2, C2.2, C3.2, C4.2, C5.2, C6.2, C7.2, C8.2, C9.2, C10.2, C13.2, C14.2, C16.2, C17.2, C20.2, C21.2, C23.2, C24.2, C26.2, C27.2, C28.2, C32.2, C33.2, C34.2, C36.2, C48.2, JP1.1, R12.2, TP2.1, U1.3 (GND), U2.2 (V-), U3.4 (AGND), U4.2 (V-), U6.2 (V-), U8.2 (V-), U9.2 (V-), U10.3 (GND)
unnamed: C25.1, C30.2, R13.1, U8.1
unnamed: C26.1, R14.1, R15.2
unnamed: C27.1, C28.1, R15.1, R16.2
unnamed: C29.1, R16.1, R17.2
unnamed: C31.2, C35.1, R20.1, U9.1
unnamed: C37.1, L1.2
unnamed: J1.7, J1.8
unnamed: C20.1, C21.1, Q1.2 (D), R10.1
unnamed: C22.1, Q1.1 (S), R12.1
unnamed: C16.1, R5.1, U2.3 (+)
unnamed: R6.2, TP3.1, U2.1, U2.4 (-), U6.3 (+)
unnamed: C15.2, R4.2, R7.1, U4.4 (-)
unnamed: U5.1 (C), U6.1
unnamed: C15.1, R4.1, R5.2, TP1.1, U4.1, U6.4 (-)
unnamed: C33.1, C34.1, R19.1, U8.5 (V+)
unnamed: C30.1, R18.2, U9.3 (+)
unnamed: C35.2, R20.2, R22.1, U9.4 (-)
unnamed: C23.1, C24.1, R11.1, U9.5 (V+)
unnamed: C36.1, R21.1, U10.1 (Vin)
VDD: C19.1, C40.1, C41.1, J1.25, J1.26, R29.1, R30.1, U7.2 (ADDR), U7.5 (VDD), U11.1 (A0), U11.8 (VCC)

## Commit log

2023-11-12 Renaming AIRDOS04 base board to sensor board.
    [AIRDOS04_base.kicad_sch, AIRDOS04_sensor.kicad_pcb, PIN_detector.kicad_sch, analogue_backend.kicad_sch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]
2023-11-12 Fix rename and improve silkscreen.
    [AIRDOS04_sensor.kicad_pcb, AIRDOS04_sensor.kicad_sch]
2023-11-12 Render previews Add testpoints.
    [AIRDOS04_sensor.kicad_pcb, AIRDOS04_sensor.kicad_sch, PIN_detector.kicad_sch, analogue_backend.kicad_sch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]
2023-11-12 change solder mask expansion and revise DRC.
    [AIRDOS04_sensor.kicad_pcb]
2023-11-12 Initial commit of detector design.
    [PIN_detector.kicad_sch, USTSIPIN03.kicad_pcb, USTSIPIN03.kicad_sch, analogue_backend.kicad_sch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]
2023-11-12 Update actions products
    [USTSIPIN03-B_Courtyard.dxf, USTSIPIN03-B_Cu.dxf, USTSIPIN03-B_Fab.dxf, USTSIPIN03-B_Mask.dxf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]
2023-11-13 Update silkscreen and title blocks.
    [PIN_detector.kicad_sch, USTSIPIN03.kicad_pcb, USTSIPIN03.kicad_sch, analogue_backend.kicad_sch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]
2023-11-13 Fix USTID
    [PIN_detector.kicad_sch, USTSIPIN03.kicad_sch, analogue_backend.kicad_sch]
2023-11-16 FIX USTIDs.
    [PIN_detector.kicad_sch, analogue_backend.kicad_sch, interface.kicad_sch]
2023-11-19 Add notes to power consumption.
    [PIN_detector.kicad_sch, analogue_backend.kicad_sch, interface.kicad_sch]
2023-11-20 Update PCB from schematics.
    [USTSIPIN03.kicad_pcb]
2023-11-20 Edit logo reference value.
    [USTSIPIN03.kicad_pcb]
2023-11-27 Flip side of pinheader connector. Resolve #7
    [USTSIPIN03.kicad_pcb, interface.kicad_sch]
2023-11-27 Swap power pins of input OpAMP. Reslove #6
    [PIN_detector.kicad_sch, USTSIPIN03.kicad_pcb]
2023-11-27 Swap MISO and MOSI traces. Resolve #4
    [USTSIPIN03.kicad_pcb, interface.kicad_sch]
2023-11-27 Attempt to improve #2.
    [USTSIPIN03.kicad_pcb]
2023-11-27 Add LDO to power 3.3V translators. Resolve #3
    [USTSIPIN03.kicad_pcb, interface.kicad_sch]
2023-11-27 Removed hand-soldering footprints for OpAmps. Rosolve #1
    [PIN_detector.kicad_sch, USTSIPIN03.kicad_pcb, analogue_backend.kicad_sch]
2023-11-27 Unmask only a sourroundings of sensing diode. Resolve #2
    [USTSIPIN03.kicad_pcb]
2023-11-27 Improve solder mask covering under sensing diode.
    [USTSIPIN03.kicad_pcb]
2023-12-05 Update PCB design title block.
    [USTSIPIN03.kicad_pcb]
2023-12-05 Uniform capacitor types.
    [analogue_backend.kicad_sch, interface.kicad_sch]
2024-05-30 Update Kicad project version.
    [PIN_detector.kicad_sch, USTSIPIN03.kicad_pcb, USTSIPIN03.kicad_sch, analogue_backend.kicad_sch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]

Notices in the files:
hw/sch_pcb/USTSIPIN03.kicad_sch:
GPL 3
